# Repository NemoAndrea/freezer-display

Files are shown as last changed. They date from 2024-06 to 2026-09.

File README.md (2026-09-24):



A common situation you find in wetlabs around the world is that there are many samples, but it is not easy to keep track of where they may be in the many freezers. Solutions generally come in two flavours:

1. A crumpled piece of damp printerpaper, covered in unreadable scribbles and crossed-out old sample labels that (allegedly) lists the contents of the freezer.
2. An online system that is well organised, but requires loading a webpage on a prehistoric netbook, setting you back 4 minutes before you finally get the information you need.

This Open Hardware design aims to provide a relatively affordable solution that aims to improve the Freezer organisation experience for those managing their Freezers with some kind of electronic system. It displays the fridge contents on an Electronic Paper Display (E-ink), and updates itself. 

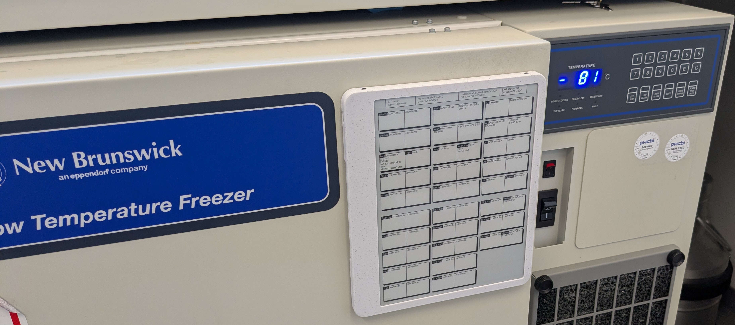
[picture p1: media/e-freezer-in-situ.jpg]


This way you not only have the advantage of having a well organised online freezer system, but **also** the advantage of having that information as **immediately available** as that outdated unreadable piece of paper that used to be on the fridge. Nobody wants a crusty piece of paper with hieroglyphics, and nobody wants to spend 3 minutes on the world's slowest computer just to find out where sample X is supposed to be stored. This solution keeps the best of both worlds.

### Hardware & Assembly

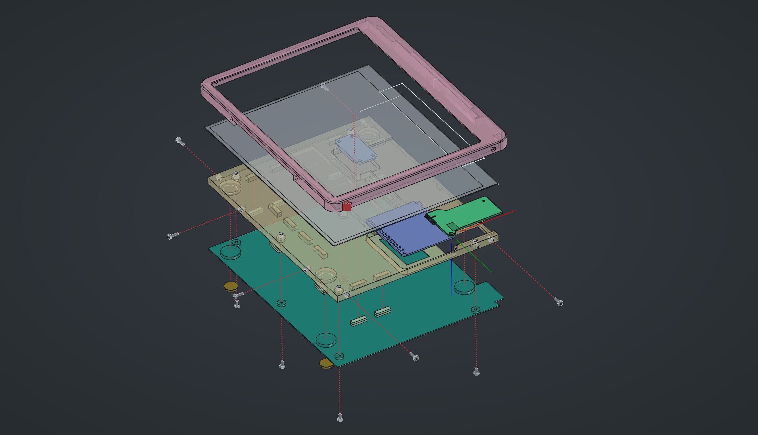
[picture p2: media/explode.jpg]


The hardware design files, [BOM](enclosure/BOM_freezer-display-assembly.csv) and assembly instructions can be found in the [enclosure](enclosure/) directory. 

Note that the device is not battery powered. 

### Software & Flashing

The code/firmware for this project can be found in the [esp](esp/) directory. The project uses the Espressif development toolchain to manage the c/c++ firmware. There you will also find instructions on the setup and on how to flash the device.

### Contributing

If you want to modify the project, I strongly suggest you use the git hooks provided in the .githooks directory. They will ensure you will always commit the most recent version of FreeCAD files and derivative items (step files, thumbnails).

```bash
git config --local core.hooksPath .githooks/
```

### Some possible future upgrades

The chosen hardware has a room for future improvements and additional functionality. In no particular order, these are some low-hanging fruit improvements.

* Add small battery, and optimise for low-power use.
* Landscape/portrait mode switching and sensor to sense this directly
* Some capacitive buttons (no ingress point, can use capacitive button pins on ESP32)
* Proper weather (or in this case Lab Goo™) sealing on the USB port
* NFC functionality to allow users to update the panel with a tap of their phone/lab device 

### Funding & Acknowledgements

This project was developed for and funded by the lab of Marileen Dogterom at the TU Delft.

Contributors:
* Nemo Andrea 

# Nix related

Use https://github.com/mirrexagon/nixpkgs-esp-dev for a shell that will enable development.

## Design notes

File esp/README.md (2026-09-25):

## High level code overview

The main operation loop is very simple; everyhting runs on a single core, as we do not need dynamic UI; we can hold up the UI updates while we run some checks or build a new screen.

We have two tasks running on the main core:
1. One task updates the UI (and triggers display refresh)
2. Another task handles getting data from the API and building the new screen; serving as a periodic background process

Task number 2 has a higher priority than task 1, and will run whenever not explicitly paused. We run this task 2 on a loop with a long pause (with `vTaskDelay()`), during which lower priority processes such as our UI code will run. 

This way we effectively only run our background processes only periodically.

```mermaid
---
config:
  flowchart:
    curve: stepAfter
---
flowchart LR
  subgraph Boot
    A[Power on]
    LOAD[Display Loading screen]
  end
  subgraph Main
    WIFI{WiFi Connected?}
    INET{Internet Connected?}
    API{API access?}
    RDR[Display Freezer Contents]
    WAIT[Sleep until time]
  end
  
  A --> LOAD
  LOAD --> WIFI
  WIFI --> INET
  WIFI -- No ----> NWIFI[Error Screen Wifi]
  INET --> API
  INET -- No ----> NINET[Error Screen Internet]
  API --> RDR
  API -- No ----> NAPI[Error Screen API]
  RDR --> WAIT
  WAIT --> WIFI

  click NWIFI "https://github.com/NemoAndrea/freezer-display/blob/main/assets/error_screens/error_screens.svg" "View Error Screen"
  click NINET "https://github.com/NemoAndrea/freezer-display/blob/main/assets/error_screens/error_screens.svg" "View Error Screen"
  click NAPI "https://github.com/NemoAndrea/freezer-display/blob/main/assets/error_screens/error_screens.svg" "View Error Screen"
```

### User Configuration

After device setup, the device can be configured by users by plugging it into any generic computer using a USB cable. The device will present itself as a USB drive containing a single plaintext config.txt file.

This file can be opened and the fields therein can be edited. Upon the next restart of the device the settings will come into effect.

You can check what values can be set in  [/fat_files/config.txt](fat_files/config.txt)

### API configuration

The current device software is set up to be rather specific for the eLabJournal system. It would be relatively straightforward to adapt it to alternative APIs, and/or other freezer layouts. In the current scope, moving to a highly generalisable system is not a priority.

If you are interested in using the project, but are daunted by the task of figuring out how to use it with another API system or would just like to exchange some thoughts, please get in touch with one of the contributors.

### Tooling & Initial Configuration

When you first connect the UnexpectedMaker board via USB it will be mounted as a circuitpython drive. We want to use the native development tools instead, and must thus wipe the circuitpython installation. 

We need to instal the python package `esptool`. I suggest you try out `uv`, but `pip` is of course perfectly adequate for the job.

Wipe circuitpython with esptool and the command

```bash
# find port with e.g. tio package
# you'll find something like /dev/ttyAMC0 (on linux)
esptool.py --port /dev/ttyACM0 erase_flash
```

To build, flash and monitor the ESP32-S3, you will also need to install the [Espressif build tools](https://docs.espressif.com/projects/esp-idf/en/latest/esp32/get-started/index.html). 

### Compiling code and workflow

Assuming you followed the configuration instructions above, you can run the following (in the current directory) to test if the code compiles:

```
idf.py build
```

If that works, you can connect the e-freezer device to your system through a USB cable. At this point, the device will likely be in the 'default' operating mode, and appear as a flash drive. To be able to reset the device and program it, you will need to prevent it from mounting as a flash drive. You can achieve this by opening the `config.txt` file that you will find on the flash drive and setting the field `skip_usb` to `true`. After saving, you can reboot the device, and now the following should work to flash new code and check the serial output:

```
idf.py flash monitor  
```

This will try to automatically detect the port of the device. It is quicker to just determine that port in advance (using e.g. `tio`) and specify it. 

```
# example port
idf.py -p /dev/ttyACM0 flash monitor  
# note that you can exit monitor with: ctrl+]
```

When flashing, you probably do not want it to turn into a flash drive after booting. While developing, make sure to change the default config.txt which gets flashed to the device (located at [/fat_files/config.txt](fat_files/config.txt)) to specify `skip_usb` = true. Remember to set it back to `false` when you are ready to put the device back out in the wild again, as otherwise users won't have a way to change those essential configuration parameters!

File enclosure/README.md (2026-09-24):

# E-Freezer Hardware Design

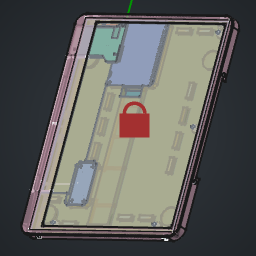
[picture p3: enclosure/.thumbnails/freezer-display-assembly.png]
Main assembly preview


explode view of the main assembly

The Hardware design for the E-freezer system is built around Waveshare's 10.3 inch high resolution E-ink panel. This panel is paired up with an ESP32-S3, connected through a shim PCB. This is all held together in an easy to 3D print enclosure that is designed to be as thin as possible. The display is held onto the target surface through embedded magnets.

See the [BOM](BOM_freezer-display-assembly.csv) for details on the parts, pricing and where to source them. For a quick image preview of the different elements of the assembly, you can check the [thumbnails](.thumbnails/) diretory.

To assemble the system, consult the [assembly instructions](assembly/README.md).

### Points of improvement

* Replacing the heated inserts with dedicated polymer/plastic screws would simplify the assembly
* The IT8951 driver chip board is not a very convenient form factor for the system. Replacing it with a more compact board, or at least one that is not difficult to desolder properly would be a massive improvement in assembly convenience.

### Tooling

Files were created using FreeCAD 1.1. To properly view the main assembly, you will also need to install the `Assembly4` workbench from the FreeCAD Addon Manager.

### BOM organisation

The BOM for the assembly is dynamically generated in FreeCAD. For this to work, custom `properties` [have to be added to each part](https://www.youtube.com/watch?v=jkNYAvFhUj8). For this project, the following *new* properties will be rendered in the BOM if included.

* `Description`: Few-word description of the part
* `Manufacturer`: self-explanatory.
* `ManufacturerNr`: the part number the manufacturer uses
* `Supplier`: If the supplier is not the manufacturer, then specify the supplier here. Otherwise, omit property.
* `SupplierNr`: self-explanatory. Omit if `Supplier` was omitted.
* `PriceEx`: the price in Euro excluding tax or shipping. Can be approximate.
* `VariantID`: if part is a component in an optional module, it should have an identifier that can be grouped in the BOM. Omit if part of the base system.
* `Comment`: optional further comments that you want to show up in the BOM. May be related to the part, its manufacturing or use, or about the sourcing of the part.

### Acknowledgements

The Unexpected Maker ESP32-S3 ProS3 STEP model was taken from the official repository. This repository [is also a submodule in the pcb directory](../pcb/esp32s3).

[^1]: This can be through laser engraving or through the application of stickers or waterslide decals. An example for such a design can be found in [the assets subdirectory](assets/enclosure-decal.svg).

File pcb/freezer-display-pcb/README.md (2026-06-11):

# Shim PCB

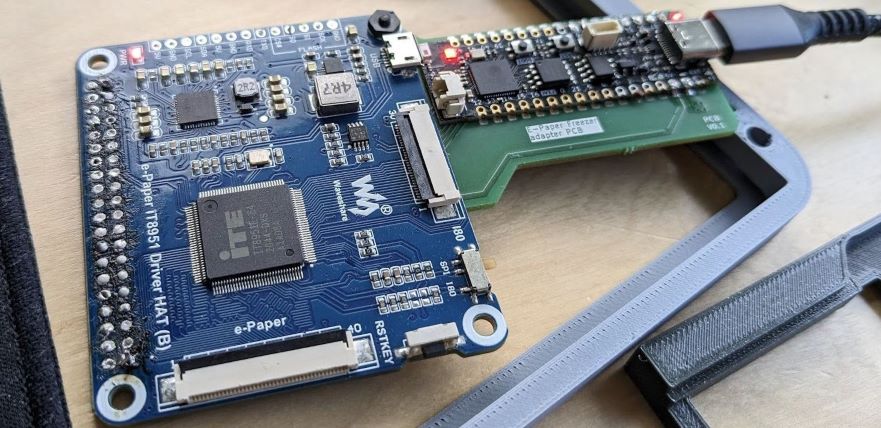
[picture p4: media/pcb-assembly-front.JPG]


The PCB for the project is a simple shim PCB, i.e. it merely serves to connect the two boards, functioning as a low-profile connector. Since we are severely constrained in terms of space, and we don't have control over the connectors on the boards that we are connecting, this seems like the best solution.

To assemble the PCB stack, you will need to remove some headers from the Waveshare board:

1. the 13 pin single row header
2. The 40-pin female Raspberry Pi-compatible header.
3. The 6-pin connector that is used for non-raspberry boards. 

The shim PCB will solder to the contact of connector 3. 

> [!TIP]
> You can temporarily add a M2.5 bolt and nut to keep the boards together and in the correct orientation during soldering. Note that the bolt will need to be removed in the final assembly.

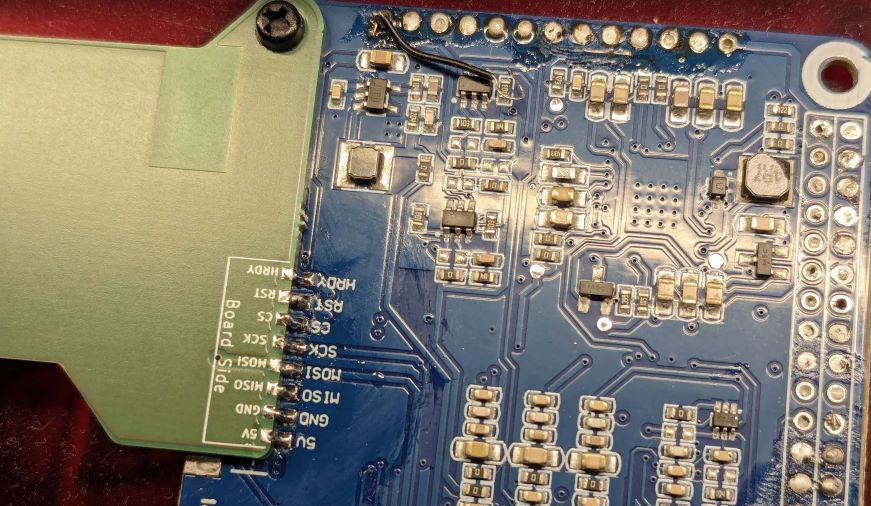
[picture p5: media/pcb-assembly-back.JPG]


### PCB Manufacturing notes

I had my boards manufactured at Aisler. Any board manufacturer that can do castellated edges should be fine. I would opt for a standard thickness. 

> [!IMPORTANT]
> The board must be manufactured with castellated edges.

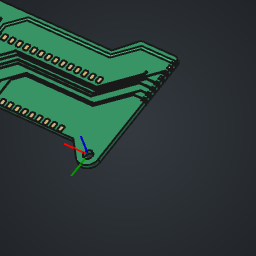
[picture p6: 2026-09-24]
enclosure/.thumbnails/PCB-freezer-display.png

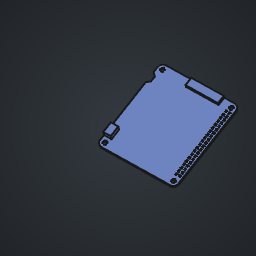
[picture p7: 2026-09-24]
enclosure/.thumbnails/IT8951_driver_board.png

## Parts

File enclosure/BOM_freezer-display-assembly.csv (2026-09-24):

Description | Manufacturer | ManufacturerNr | Supplier | SupplierNr | Quantity | PriceEx | Comment
3D printed part (internal frame) | N/A | N/A | N/A | N/A | 1 | 4 | N/A
3D printed frame (external part) | N/A | N/A | N/A | N/A | 1 | 4 | N/A
3D printed back panel | N/A | N/A | N/A | N/A | 1 | 4 | N/A
Anti-slip pad | =3 M | SJ5312 | SKS GmbH | 10497 | 4 | 1.82 | N/A
10.3inch E-paper display | Waveshare | 18434 | Welectron | WS3-018434 | 1 | 192.44 | N/A
E-paper FPC adapter board | N/A | N/A | N/A | N/A | 1 | N/A | Included with the E-paper display.
N/A | N/A | N/A | N/A | N/A | 1 | N/A | N/A
E-paper IT8951 driver board | N/A | N/A | N/A | N/A | 1 | N/A | Included with the E-paper display. Requires some desoldering to be used in the assembly.
Simple Custom Shim PCB | Aisler | N/A | N/A | N/A | 1 | 13.95 | See the PCB directory in the project repo for ordering files. Price is for the MOQ of 3 boards.
ESP32-S3 Board (ProS3) | Unexpected Maker | PS3D-01 | tinytronics | 5850 | 1 | 19.01 | N/A
M3 threaded inserts 3mm depth | cnc kitchen | 4270002316416 | N/A | N/A | 12 | 0.75 | N/A
Neodymium Magnet 4x4x15mm | supermagnete.de | Q-15-04-04-MN | N/A | N/A | 8 | 0.67 | N/A
M2.5 8mm screw (ISO7045) | N/A | N/A | N/A | N/A | 6 | N/A | N/A
M2.5 5mm screw (ISO7045) | N/A | N/A | N/A | N/A | 6 | N/A | N/A

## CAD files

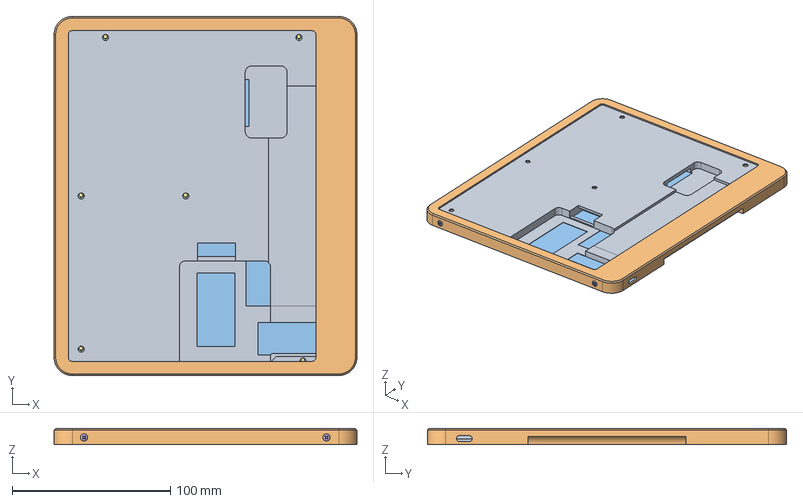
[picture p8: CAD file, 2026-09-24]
enclosure/freezer-display-assembly.FCStd
191.2 x 226.7 x 10.2 mm
internal-frame
external-frame
Back-panel
M2.5x3.74-Insert x 12
magnet x 8
M2.5x8-Screw010 x 6
M2.5x5-Screw x 6

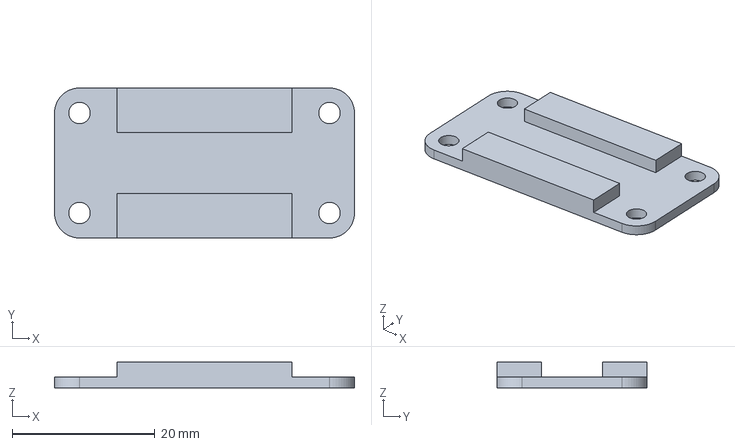
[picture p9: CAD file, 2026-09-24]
enclosure/FPC_to_FFC_board.FCStd
42.0 x 21.0 x 3.60 mm

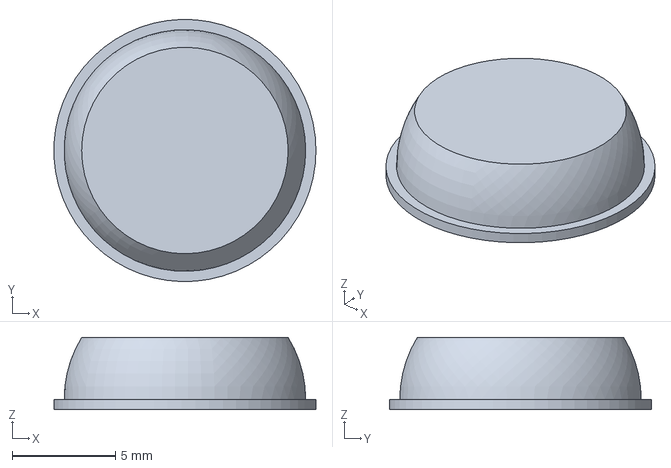
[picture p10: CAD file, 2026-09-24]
enclosure/3M_bumpon_SJ5312.FCStd
12.7 x 12.7 x 3.50 mm

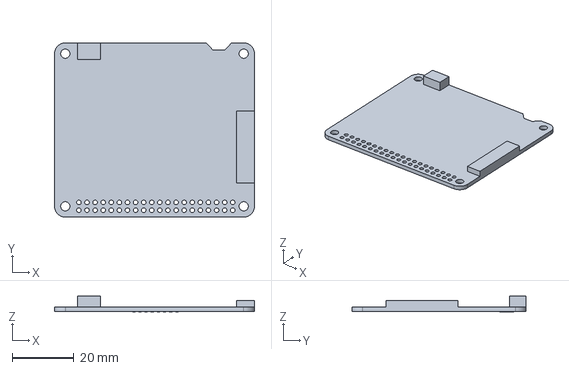
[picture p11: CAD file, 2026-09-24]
enclosure/IT8951_driver_board.FCStd
65.0 x 56.6 x 5.10 mm

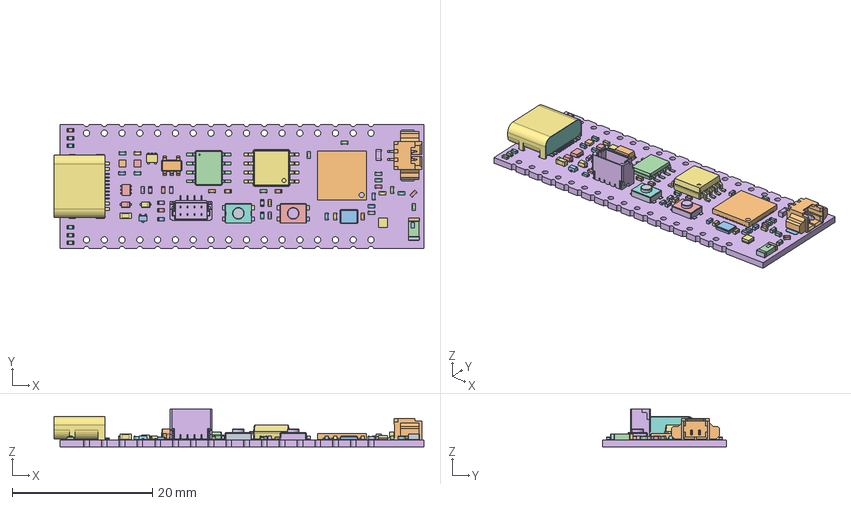
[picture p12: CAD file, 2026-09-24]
enclosure/UnexpectedMaker_ProS3.FCStd
52.8 x 17.8 x 5.38 mm
ProS3_STEP_MAKER PCB

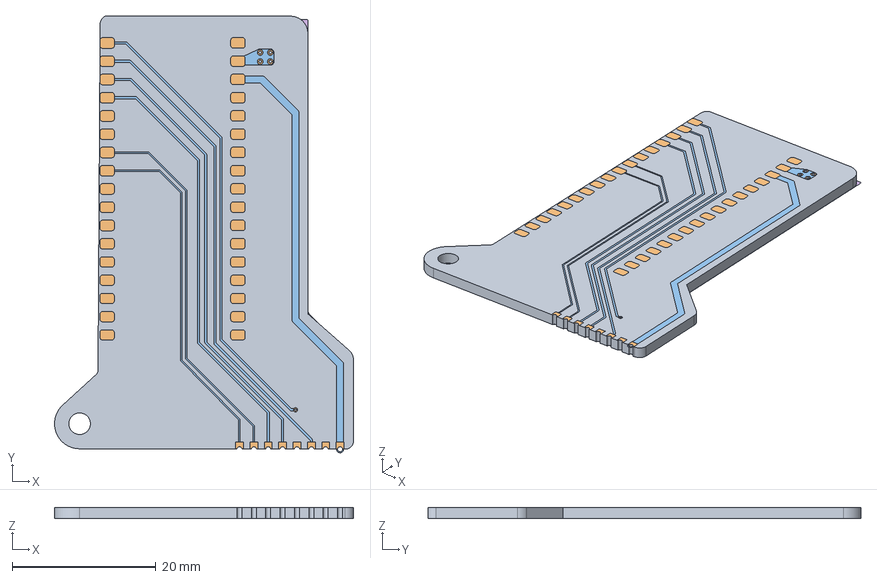
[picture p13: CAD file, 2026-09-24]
enclosure/PCB-freezer-display.FCStd
41.6 x 60.8 x 1.64 mm
Pcb_e244
topPads_e244_cut
topTracks_e244
botPads_e244_cut
botTracks_e244
botZones_e244

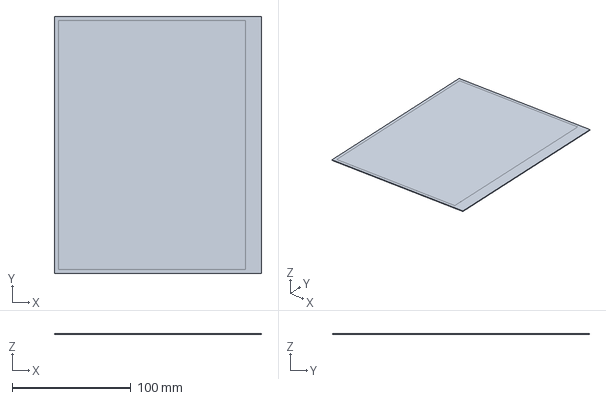
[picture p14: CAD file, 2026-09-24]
enclosure/waveshare_10.3_1872x1404_EPD.FCStd
174.4 x 216.7 x 0.78 mm

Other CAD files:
enclosure/PCB-assembly.FCStd

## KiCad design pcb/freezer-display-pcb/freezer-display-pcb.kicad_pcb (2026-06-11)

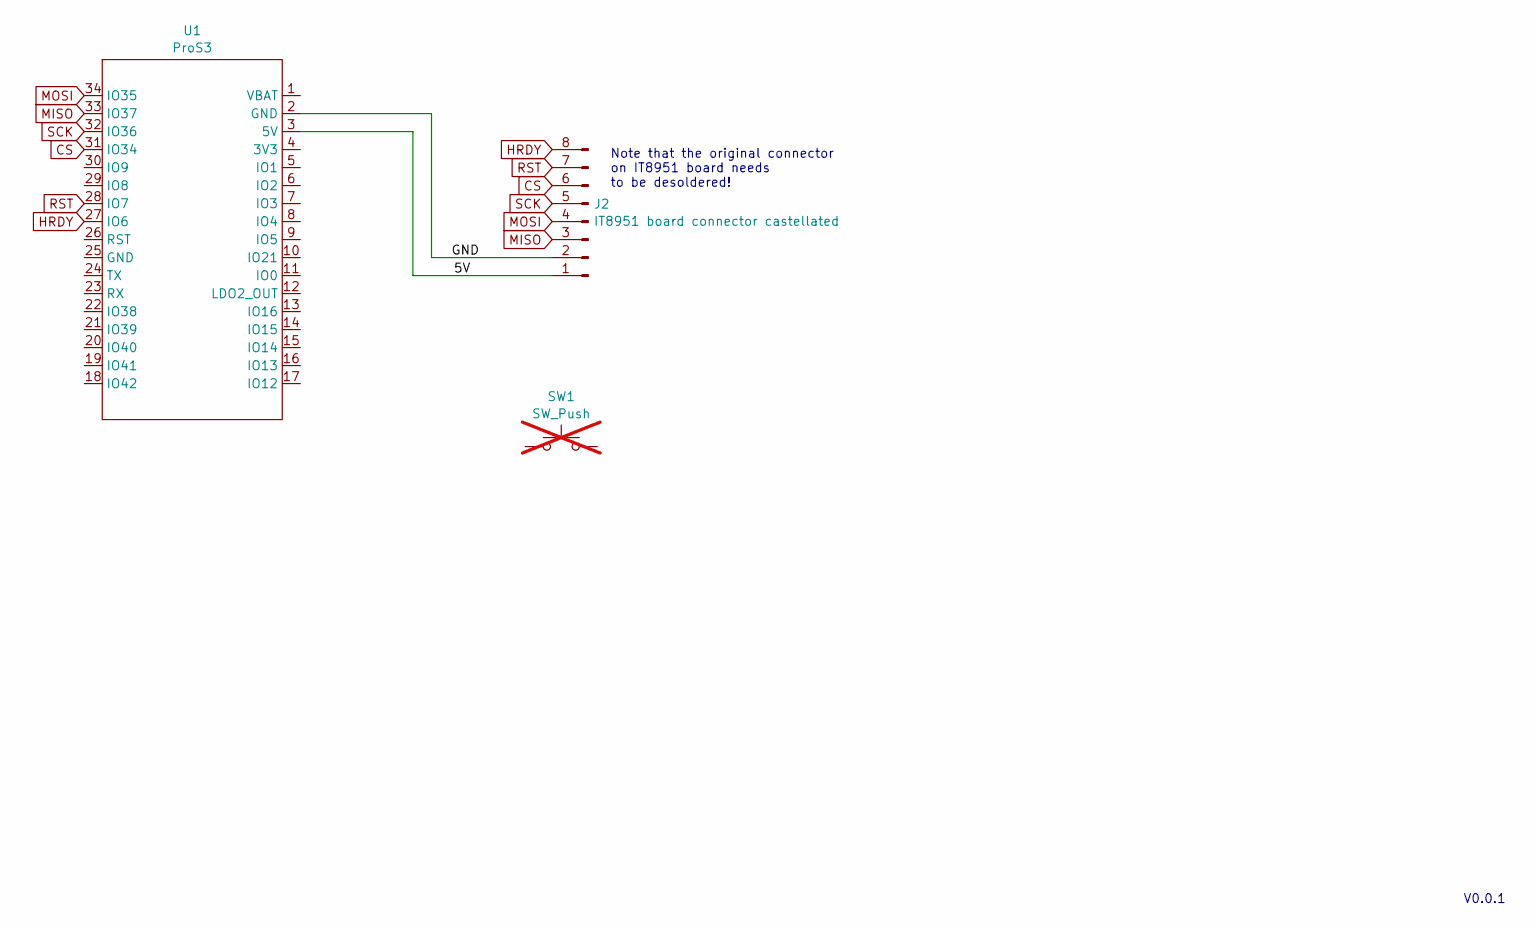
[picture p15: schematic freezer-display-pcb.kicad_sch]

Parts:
J2: IT8951 board connector castellated; IT8951-diver-castellated
SW1: SW_Push; SW_Tactile_SPST_Angled_PTS645Vx83-2LFS; Mouser 506-2-1825027-0; not fitted
U1: ProS3; ProS3_SMD

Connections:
/5V: J2.1, U1.3 (5V)
/GND: J2.2, U1.2 (GND)
CS: J2.6, U1.31 (IO34)
HRDY: J2.8, U1.27 (IO6)
MISO: J2.3, U1.33 (IO37)
MOSI: J2.4, U1.34 (IO35)
RST: J2.7, U1.28 (IO7)
SCK: J2.5, U1.32 (IO36)

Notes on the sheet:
V0.0.1
Note that the original connector on IT8951 board needs to be desoldered!

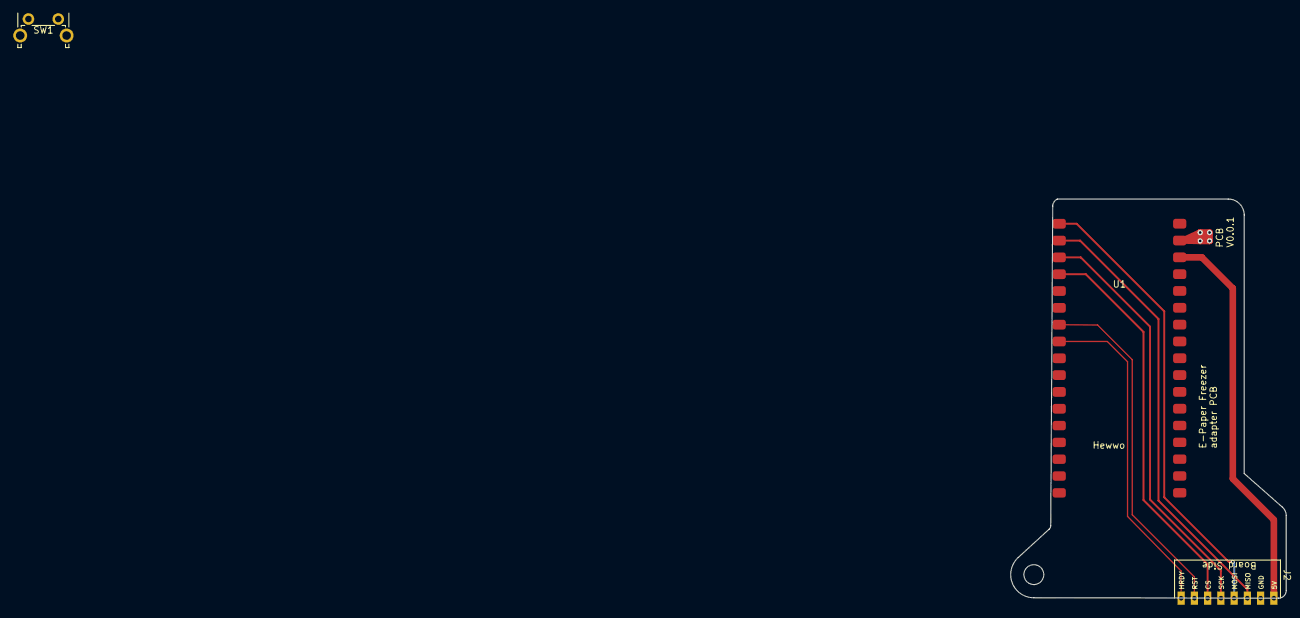
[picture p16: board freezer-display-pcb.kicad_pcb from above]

Board: 2 copper layers, 41.6 x 60.3 mm, 3 parts (0 on the bottom side), 8 nets.

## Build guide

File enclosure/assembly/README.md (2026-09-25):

# Assembly Guide

## Required tools

* Infared/hot air solderin station
* Soldering Setup
* Screwdriver (for philips-type screws, or whatever M2.5 screws you ordered)
* Safety goggles
* [optional] kapton tape
* [optional] Painters tape or other thin tape or glue

## Steps

Before the system can be assembled, we must first remove some of the headers from the IT8951 driver board. This can be very tricky, as the headers are large elements that require heating of a large area of the board. An infared heater or hot air station is absolutely required. The (1) yellow header array (visible in image below), the (2) raspberry-pi-compatible header (on the underside of the board in image below) and (3) a connector (on the underside of the board in the image below) must be removed.

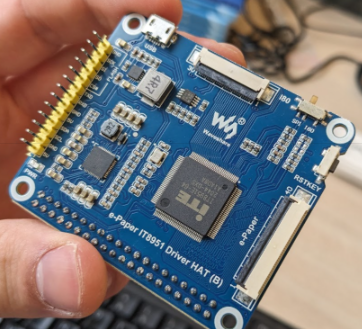
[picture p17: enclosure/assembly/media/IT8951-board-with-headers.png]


The Pro-S3 board must then be soldered onto the shim PCB as shown in the FreeCAD file and the image below:

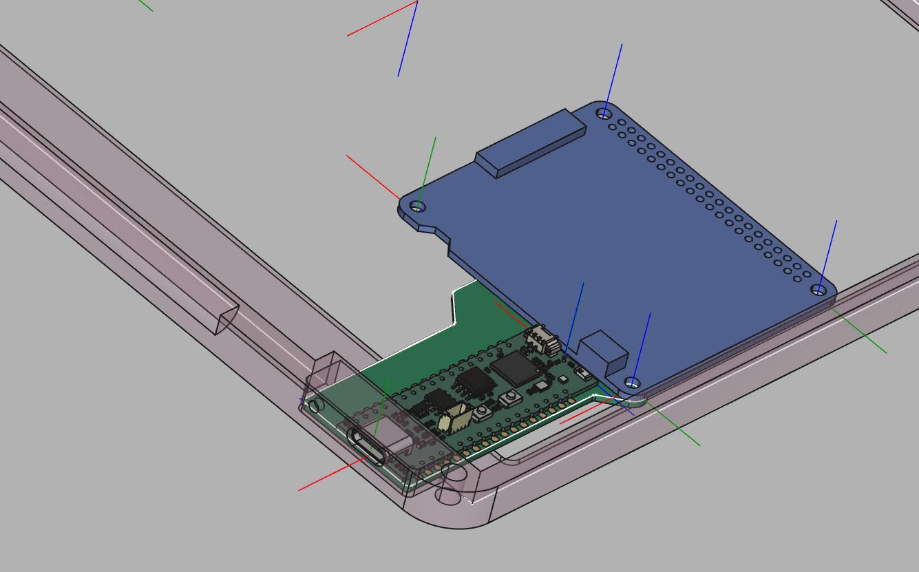
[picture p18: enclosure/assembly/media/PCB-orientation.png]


The IT8951 driver board must also be soldered onto the shim PCB. This can be tricky, as the contact area is small. To make this easier, **temporarily** screw/clamp the boards together using the aligned circular hole in the corners of both boards. make sure to remove the clamping source afterwards. It should look something like this (minus the solder bridging).

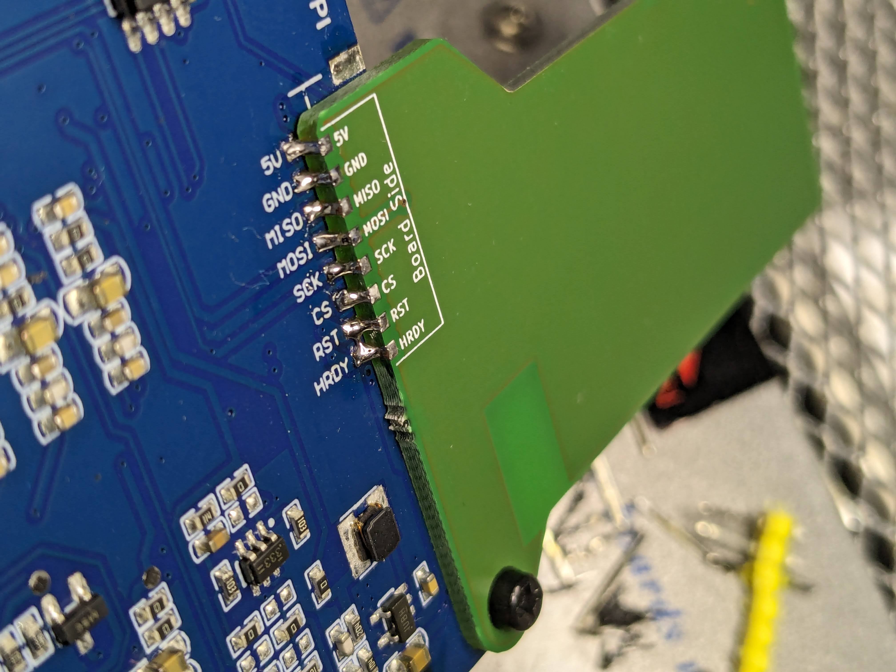
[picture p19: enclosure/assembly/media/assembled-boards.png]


> [!TIP]
> At this point, I would flash the firmware and see if the system behaves as expected before continuing assembly.

In the 3D printed parts, insert the threaded inserts with a soldering iron. Be careful not to tilt them too far out of axis; the tolerances are not critical, but it is very easy to tilt the insert due to the limited amount of material around each insert point.

Now we can just assemble the whole thing. 

> [!WARNING]
> The Flexible PCB that is coming off the display is fragile. Be careful when handling or bending it.

We want to start by placing the (fragile) display into the outer frame. Note that the display has a protective cover film -- you may want to remove it. First insert the part of the display into the side of the E-freezer that is furthest from the charging port. Then lower it fully into the slot, carefully bending the Flex PCB

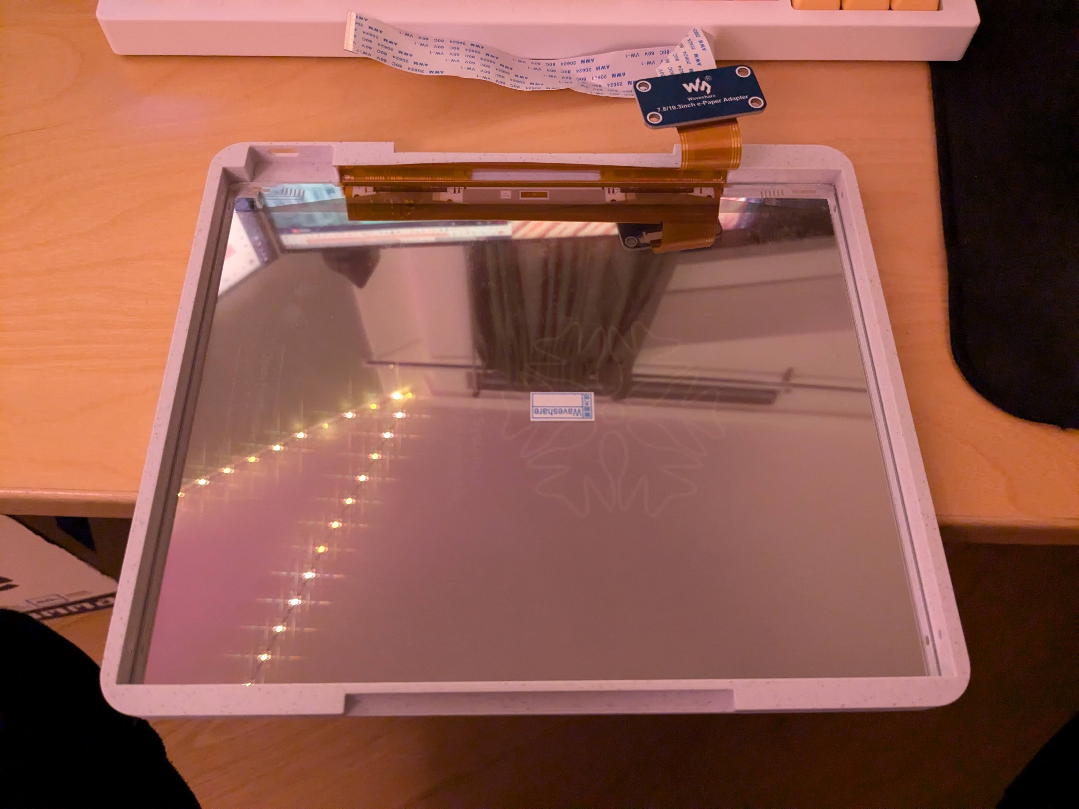
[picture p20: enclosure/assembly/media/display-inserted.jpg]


Next, you will want to disconnect the write ribbon cable from the IT8951 driver board, and route it through the 3D-printed inner frame. You may have to bend the cable at an uncomfortable angle. Try to maximise the bending radii. Once the ribbon cable is routed, reconnect the IT8951 board. This may all be a bit tricky and require some dexterity as the cables are short, and you will want to pay attention to the Flex PCB of the display. It should look something like this when done correctly:

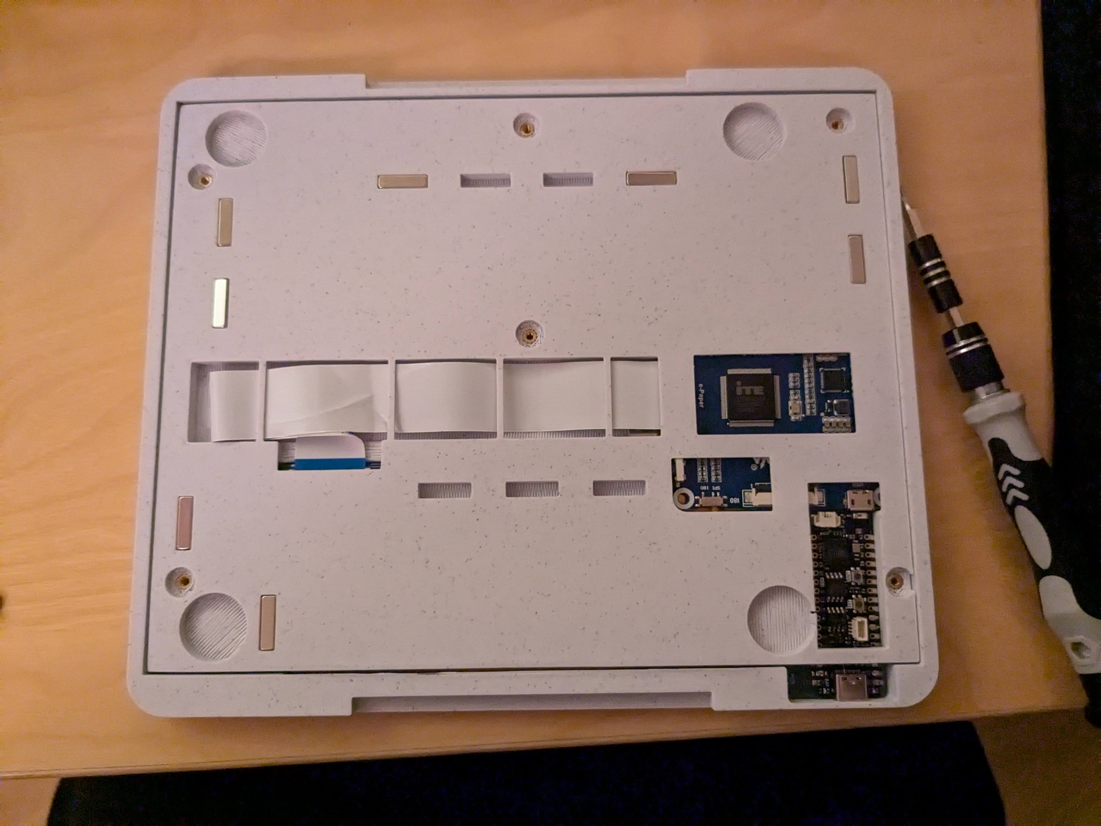
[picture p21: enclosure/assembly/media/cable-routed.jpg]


> [!TIP]
> If you want to be super safe, you can cover the side of the IT8951 board that contacts the display with some Kapton Tape. 
> That way it will not scratch the display or cause shorts[^2]. It also helps keep things in place as you try to fold it all together. Below an example with an older revision of the internal frame.
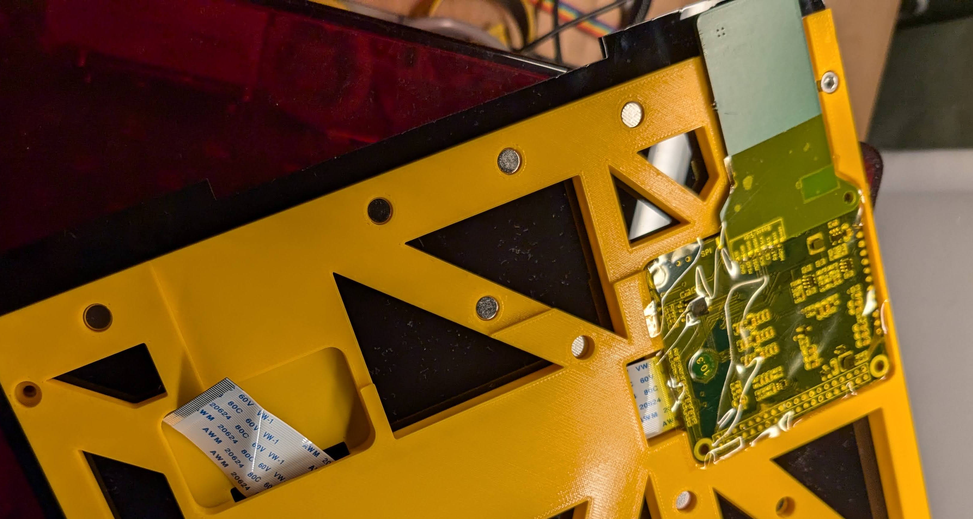
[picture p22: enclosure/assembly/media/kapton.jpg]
> 

> [!CAUTION]
> Always wear safety goggles when handling neodymium (or strong) magnets.

At this stage, the magnets can be inserted. Make sure to have all their polarities point in the same way. Be careful with the magnets; they will want to shoot out of the pockets. Adding some thin painters tape or other way to keep them in the pocket is a good idea.

After adding the magnets, you can screw everything together and add the anti-slip pads to the back-panel.

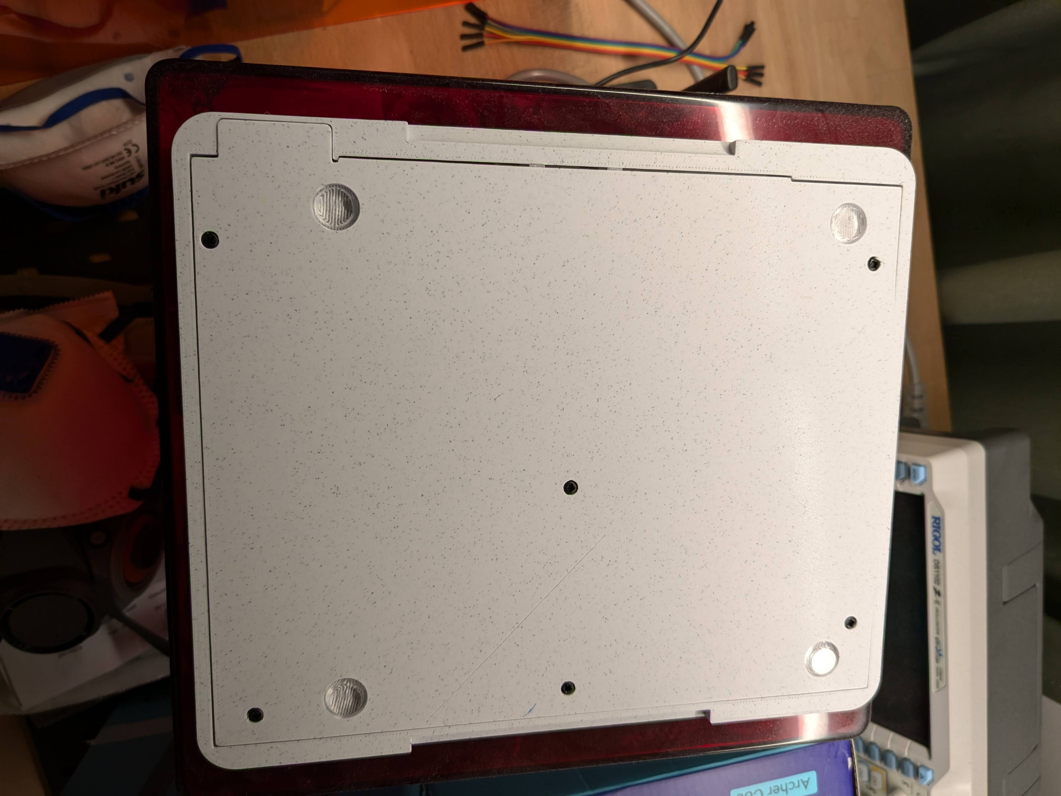
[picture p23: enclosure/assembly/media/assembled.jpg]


To cosmetically finish off the part, or to provide some instructions and guidance for the user, you could apply text to the 3D printed parts.[^1]

[^1]: This can be through laser engraving or through the application of stickers or waterslide decals. An example for such a design can be found in [the assets subdirectory](../assets/enclosure-decal.svg).
[^2]: I don't think shorting is very likely, but with kapton tape it will be safe even under heavy abuse.

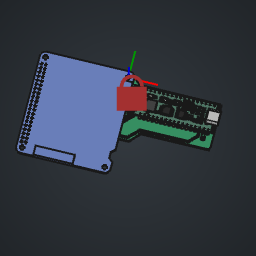
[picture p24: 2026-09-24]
enclosure/.thumbnails/PCB-assembly.png

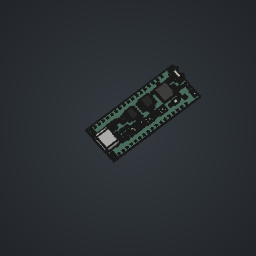
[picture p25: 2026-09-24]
enclosure/.thumbnails/UnexpectedMaker_ProS3.png

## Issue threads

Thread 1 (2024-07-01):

### ISSUE TITLE
Possible collaboration?

### ISSUE THREAD

**Issue by regerohan** [NemoAndrea/freezer-display#1]
Hi Nemo!
This is similar to something I had in mind but for a different application.
And I would like to use your project as a base for that!
Let me know if you need any help to speed things up :)

**Comment by regerohan** [comment]
I was also wondering how you planned to add/update the samples?

**Comment by NemoAndrea** [comment]
Heya, sounds nice! I will add you to the work in progress album so you can check out where I am at. 

I am waiting for some parts to come in (allowing for hopefully a prototype that is functionally complete), and then I will work on the software again. I think in basic form the software will be quite simple; the only thing that really still needs doing is (1) efficient way to display text into buffer and (2) porting the SPI data generation to C or making the python a lot faster.

**Comment by NemoAndrea** [comment]
Oh, and if you have access to a vacuum forming setup - let me know 😉

**Comment by regerohan** [comment]
Yes, I've access to a vacuum forming setup :)

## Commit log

2024-05-09 working code that refreshes the display
    turns out the main usb supply to microcontroller does not have enough power to reset the display or something like that. Unfortunate.
2024-05-11 Add components for enclosure design and early concept
    Add 3D models for the components that go into the enclosure deisng and make a rough early concept for the enclosure. Added the ProS3 board as a submodule for footprints, 3D model and provenance.
    [FPC_to_FFC_board.FCStd, IT8951_driver_board.FCStd, UnexpectedMaker_ProS3.FCStd, freezer-display-assembly.FCStd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]
2024-05-12 New enclosure design
    New design that involves around polycarbonate-all-around for sealing and cleanability Early work on PCB design.
    [IT8951_driver_board.FCStd, PCB-assembly.FCStd, PCB-freezer-display.FCStd, UnexpectedMaker_ProS3.FCStd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]
2024-05-12 Add shim PCB
    Simple PCB that takes the role of low-profile wiring. In theory future buttons and LEDs could be added, but will not be considered for now.
    [PCB-assembly.FCStd, PCB-freezer-display.FCStd, freezer-display-pcb.kicad_pcb, freezer-display-pcb.kicad_sch]
2024-05-12 First version of complete design
    Design complete in priciple except for absence of magnet spots. Will probably still need some revisions and test prints to get everything dialed in.
    [IT8951_driver_board.FCStd, PCB-assembly.FCStd, PCB-freezer-display.FCStd, freezer-display-assembly.FCStd]
2024-05-14 Increased tolerances on parts & minor tweaks
    Increased tolerances on parts, added groove for FPC cable bulk and made FPC groove 1mm wider. All based on 3D printed testfit.
    [freezer-display-assembly.FCStd]
2024-06-09 Fixed swapped net labels
    MISO and MOSI nets were swapped, but the functionality of the PCB was correct. Now updated to avoid confusion. PCB design has been assembled and seems to work. Added basic documentation for the PCB.
    [freezer-display-pcb.kicad_pcb, freezer-display-pcb.kicad_sch]
2024-06-18 Adjust enclosure dimensinos to minimise cable stress
    Old design files put a lot of stress on FPC which should be avoided.
    [FPC_to_FFC_board.FCStd, IT8951_driver_board.FCStd, PCB-assembly.FCStd, UnexpectedMaker_ProS3.FCStd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]
2024-06-23 Redo enclosure design to avoid backside screws
    Redid the enclosure design to avoid having screws protrude from the back; which would require stronger magnets than strictly needed. Now threaded inserts are put into the acrylic backpanel, allowing 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
    [FPC_to_FFC_board.FCStd, IT8951_driver_board.FCStd, PCB-assembly.FCStd, UnexpectedMaker_ProS3.FCStd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]
2024-06-23 Remove legacy designs
    Some older design iterations were still part of the document. Removed them for clarity
    [freezer-display-assembly.FCStd]
2024-11-09 Add 3M bumpon friction pad design file
    A simple design file for product available in the 3M SJ5300 BL Bumpon mini-pack
    [3M_bumpon_SJ5312.FCStd]
2024-11-09 3D printed backpanel design
    First steps towards printed backside panel (as opposed to lasercut)
    [3M_bumpon_SJ5312.FCStd, freezer-display-assembly.FCStd]
2024-11-21 Improve mechanical rigidity
    Added two extra screws on the side of the frame to aid with rigidity. Added some cutout pockets in the frontpanel for the backpanel to slot into - to prevent the backpanel from flexing too much. Also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
    [freezer-display-assembly.FCStd]
2026-06-11 update main README for mode to linux development
    [freezer-display-pcb.kicad_pcb, freezer-display-pcb.kicad_sch]
2026-06-21 Reproduce demo code IT8951
    Working reproduction of https://github.com/pvginkel/it8951-esp32. It seems like GPIO pin 35 is damaged on my board. Switching a bypass wire from GPIO 4->35 reproduces expected behaviour from example 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
2026-06-22 First somewhat functional LVGL code
    Things are drawn to display after migrating sample code of Pieter van Ginkel to LVGL 9, but there are still clear artifacts. WIll move to PSRAM.
2026-06-29 Create custom partition file
    Too many libraries and assets make the main image too big. Increased partition size to accomodate (plenty of flash storage left)
    [partitions.csv]
